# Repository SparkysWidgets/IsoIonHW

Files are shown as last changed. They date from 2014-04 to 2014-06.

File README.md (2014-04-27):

Welcome To: IsoIon Hardware Repo!!
================================

##### Note: This is for the IsoIon Hardware Version 01 Branch

IsoIon Hardware Design Files in EAGLE. IsoIon is the first and only fully open source ISE interface with galvanic isolation. It only requires a single supply on the primary end, meaning no more pesky dual supply solutions with wallwarts or DC-DC converters everywhere. IsoIon is an Ion Selective Electrode Interface with 127 steps of programmable gain control which allows it to adapt to most ISE style probes. Great care was taken during part selection to create the best all around solution with great performance for the price. All components have been proven over the last several months(if not years) via other projects (MinipH, ISOBreakout, I2CADCBreakout, etc...). IsoIon is meant to be used in a wide array of installations from commercial products, Arduino and RaspPi Projects to lab usage. If you need to interface pH, Galvanic DO, ORP, Nitrate, or most other ISE style probes this is the interface for you!!!! Its meant to interface most platforms and even contains a Seeed Grove style connector for easy integration into the Grove environment.
Please respect the licensing on these designs, we all loose if licensing inst followed and proper credit is not given!

Schematic and General Info
-------------------------
##### The initial schematic is a bit messy sorry will clean up.

- Most of this design is proven from my other works, this is the culmination of lots of research and testing (others have copied my work beware of their closed designs)
- Single supply Isolation is provided by the pair of AD micromodules ADUM6010 iso DC-DC converter and the ADUM1251 I2C isolation module for hotswapping I2C systems on a I2C bus 
- Analog front end is boosted with an I2C digital pot in place of on leg of the gain control feedback loop (this is a proper reostat digipot IC). This gives us gain control so we can select what type of probe to interface pretty ingenious Special Thanks to Practical Maker for showing me a simpler way. I just automated his method and adjusted it to match how I interface probes (We both do it slightly different, difference is good in my opinion keep up your work PM!!!!)
- Negative voltage rail generation has been slightly improved I added in an output filter network that was tested to help a bit of the noise getting through to the amplification stage.
-I've updated the design to use a fixed 3.0v precision voltage reference ad the ADC VDD/VREF input, while the op-amp will still operate at 5v rails. I am pushing us up and out of the noise floor on both rails, you won't see this much elsewhere and probably wont until this proliferates. This design still meets my requirements for 2.7 to 5.5 VIN!
- Final amp stage to ADC has been properly filtered as per TI- app notes for matching ADCs to conditioning amps
- Reverse voltage protection using Afrotechmods Pfet method! Its all about VGS vs VDS hehe!

Board Layout Info
-------------------------
##### Form factor is the same width as the Mini line but was made a bit longer to accommodate the Isolation section from my ISOBreakout designs.

- Standard 2.54mm pitch header and Grove style connector is left in place
- Careful consideration on both part placement and trace layout is very important to overall success, we are dealing with 2 fully isolated ground planes.
- DC-DC converter topologies exist on this board, some will be in close proximity to the input stage. the Negative voltage rail generator is based on a charge pump at 250Khz we want to filter this out at the -5v output, but we want only enough bypass capacitance to filter these harmonics and a bit more general op-amp operation, since we have 1uF already at the chargepump. built RC network around .1uF as close to op-amp as possible, with 1uf supply at charge pump out put. Keep these traces short and surrounded by ground plane. 
- Proper placement and layout of the analog front end is crucial to achieve best performance characteristics. Guard rings must be used around the input leg of BNC, this is so often overlooked it makes me sad. Am I the only one who reads the app-notes datasheets and op-amp books??? If your probe is going to ground to your plane(ie non differential or instrumentation topo), make sure you control the current return path (this really isnt too much of a concern on pH interfacing but other probes can source mAs)
- As per above, Op-amp is mounted underside with minimal trace length to keep complex impedances/reactances to minimum, this lets us keep all the "hot" end of amplification stage inside a guard ring. As per op-amp operation the feedback loop output(into the - pin) will drive the guard ring to the same potential as the probe input pin so everything inside the ring will have enough drive to keep it there despite noise sources and outside influences, pretty cool huh! See layout of board to get a better idea, this is how an ideal guard ring should work (including both sides as shown with the small ring on top)
- The rest of the layout is just based on functional placements with minimal trace routing work, via count inst really an issue so burn them up if you want to make really nicely couple ground planes.
- Some test pad experimentation with the obvious ones marked in new "parts" GND, V+, V- with offset and pHVout test points near their usage points.
- REMEMBER ISOLATED GROUNDS DONT CROSS THEM, take measurements from each side with respect to its ground(reference) it is important to remember or else you may burn up the isolation ICs 
- Revers voltage protection added to both header VIN inputs, using a simple p-channel mosfet to since reverse voltages and switch off.

Errata
-------------------------

##### Just a quick list of current issues
- Mostly untested as a whole, but each part has been working for a while are are mature projects
- Silkscreen  as always could use some improvements.
- Care might be needed in measuring the digipots wiper to calculate the gain more accurately
- This thing is going to be awesome and change how we think of plain old pH interfaces!!!!!

Firmware
-------------------------

- Take a look in [isoIon's Firmware Repo](https://github.com/SparkysWidgets/IsoIonBFW) For Arduino!
- Check out my USB pH interface[LeoPhi](http://www.sparkyswidgets.com/Projects/LeoPhi.aspx) for a powerful and easy to use USB PH Probe interface!

Basic Usage
-------------------------

License Info
-------------------------

<p>This is a fully open source project released under the CC BY license</p>
<br />
<span xmlns:dct="http://purl.org/dc/terms/" property="dct:title">IsoIon</span> by <a xmlns:cc="http://creativecommons.org/ns#" href="www.sparkyswidgets.com" property="cc:attributionName" rel="cc:attributionURL">Ryan Edwards, Sparky's Widgets</a> is licensed under a <a rel="license" href="http://creativecommons.org/licenses/by-sa/3.0/deed.en_US">Creative Commons Attribution-ShareAlike 3.0 Unported License</a>.<br />
Based on a work at <a xmlns:dct="http://purl.org/dc/terms/" href="/portfolio-item/ion-selective-electrode-interface" rel="dct:source">https://www.sparkyswidgets.com/portfolio-item/ion-selective-electrode-interface</a>

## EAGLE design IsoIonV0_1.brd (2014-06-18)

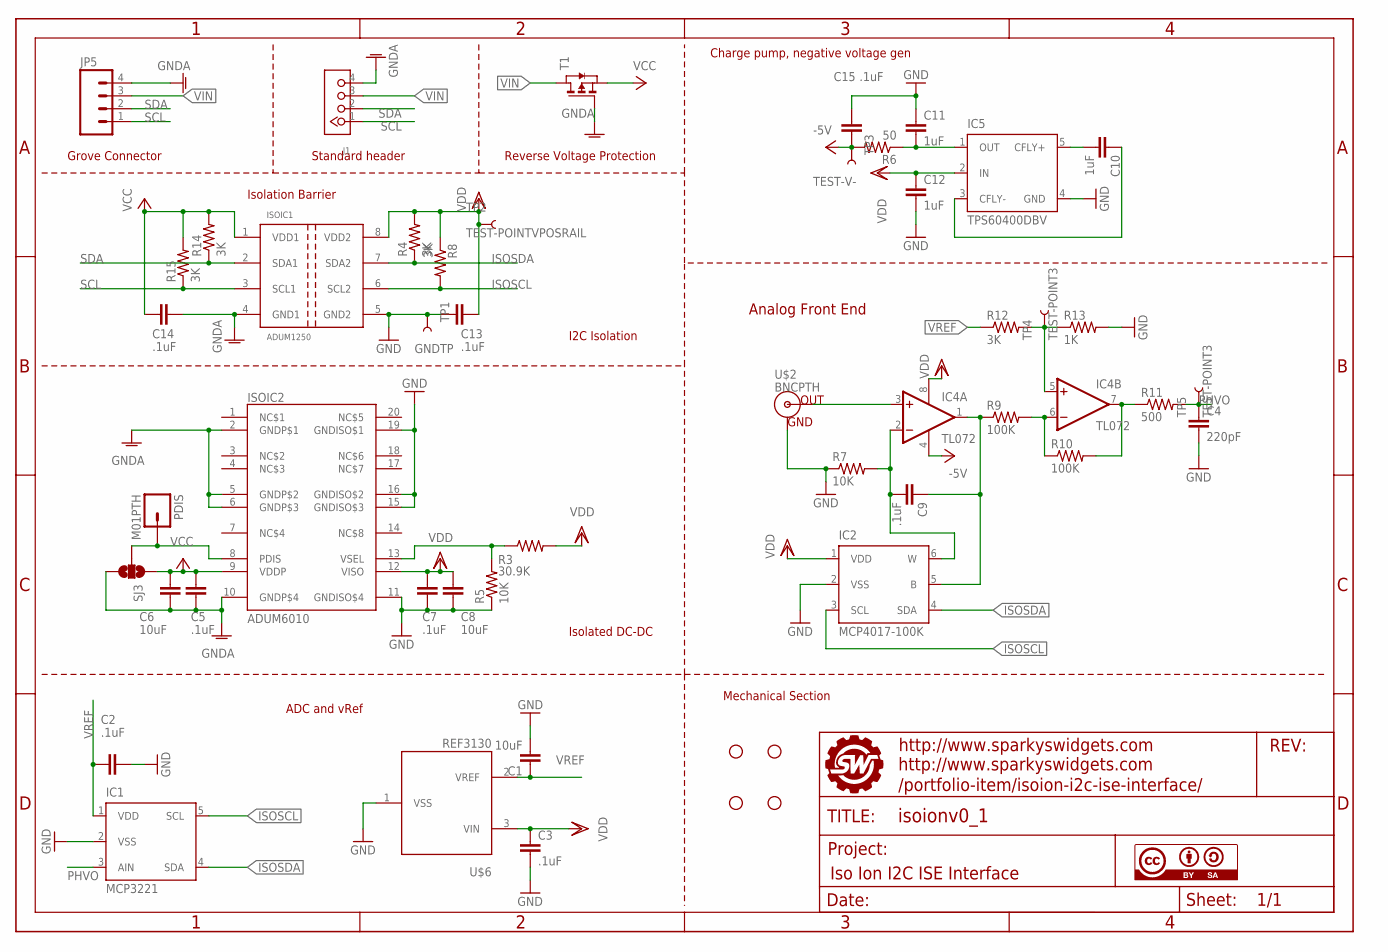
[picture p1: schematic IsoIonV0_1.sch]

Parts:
C1, C6, C8: 10uF; 0805
C2, C3, C5, C7, C9, C13, C14, C15: .1uF; 0805
C4: 220pF; 0805
C10, C11, C12: 1uF; 0805
IC1: MCP3221; SOT23-DBV
IC2: MCP4017-100K; SC70
IC4: TL072; SO08@1
IC5: TPS60400DBV; SOT23-DBV
ISOIC1: ADUM1250; SO08
ISOIC2: ADUM6010; SSOP20
J1: TWIG-4P-2.0-2.0; 4P-2.0
JP1, JP2, JP3, JP4: STAND-OFF
JP5: M04PTH; 1X04
PDIS: M01PTH; 1X01
R3: 30.9K; 0805
R4, R8, R12, R14, R15: 3K; 0805
R5, R7: 10K; 0805
R6: 50; 0805
R9, R10: 100K; 0805
R11: 500; 0805
R13: 1K; 0805
SJ3: SOLDERJUMPER_2WAYPASTE2&3; SJ_3_PASTE2&3
T1: PMOSSOT23; SOT-23
TP1: GNDTP; TEST_GND
TP2: TEST-POINTVPOSRAIL; TEST_V+
TP3: TEST-V-; TEST_V-
TP4, TP5: TEST-POINT3; PAD.03X.03
U$1: FRAME_ISOION; SWPCBLOGOWITHINFO
U$2: BNCPTH; BNC
U$3: CC-BY-SA
U$6: REF3130; SOT-23

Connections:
-5V: C15.2, IC4.4 (V-), R6.2, TP3.P$1
GND: C1.2, C2.1, C3.2, C4.2, C7.2, C8.2, C11.1, C12.2, C13.1, C15.1, IC1.2 (VSS), IC2.2 (VSS), IC5.4 (GND), ISOIC1.5 (GND2), ISOIC2.11 (GNDISO$4), ISOIC2.15 (GNDISO$3), ISOIC2.16 (GNDISO$2), ISOIC2.19 (GNDISO$1), R5.1, R7.1, R13.2, TP1.P$1, U$2.GND, U$6.1 (VSS)
GNDA: C5.2, C6.2, C14.1, ISOIC1.4 (GND1), ISOIC2.2 (GNDP$1), ISOIC2.5 (GNDP$2), ISOIC2.6 (GNDP$3), ISOIC2.10 (GNDP$4), J1.4, JP5.4, SJ3.3, T1.3 (G)
ISOSCL: IC1.5 (SCL), IC2.3 (SCL), ISOIC1.6 (SCL2), R8.2
ISOSDA: IC1.4 (SDA), IC2.4 (SDA), ISOIC1.7 (SDA2), R4.1
unnamed: IC4.5 (+IN), R12.2, R13.1, TP4.P$1
unnamed: IC4.7 (OUT), R10.2, R11.1
unnamed: IC4.6 (-IN), R9.2, R10.1
unnamed: ISOIC2.8 (PDIS), PDIS.1, SJ3.2
unnamed: ISOIC2.13 (VSEL), R3.1, R5.2
unnamed: C11.2, IC5.1 (OUT), R6.1
unnamed: IC4.3 (+IN), U$2.S (OUT)
unnamed: C9.2, IC2.6 (W), IC4.2 (-IN), R7.2
unnamed: C9.1, IC2.5 (B), IC4.1 (OUT), R9.1
unnamed: C10.1, IC5.3 (CFLY-)
unnamed: C10.2, IC5.5 (CFLY+)
PHVO: C4.1, IC1.3 (AIN), R11.2, TP5.P$1
SCL: ISOIC1.3 (SCL1), J1.1, JP5.1, R15.1
SDA: ISOIC1.2 (SDA1), J1.2, JP5.2, R14.1
VCC: C5.1, C6.1, C14.2, ISOIC1.1 (VDD1), ISOIC2.9 (VDDP), R14.2, R15.2, SJ3.1, T1.2 (S)
VDD: C3.1, C7.1, C8.1, C12.1, C13.2, IC2.1 (VDD), IC4.8 (V+), IC5.2 (IN), ISOIC1.8 (VDD2), ISOIC2.12 (VISO), R3.2, R4.2, R8.1, TP2.P$1, U$6.3 (VIN)
VIN: J1.3, JP5.3, T1.1 (D)
VREF: C1.1, C2.2, IC1.1 (VDD), R12.1, U$6.2 (VREF)

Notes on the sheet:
Grove Connector
Charge pump, negative voltage gen
Analog Front End
Isolation Barrier
Reverse Voltage Protection
Standard header
I2C Isolation
Isolated DC-DC
ADC and vRef
Mechanical Section

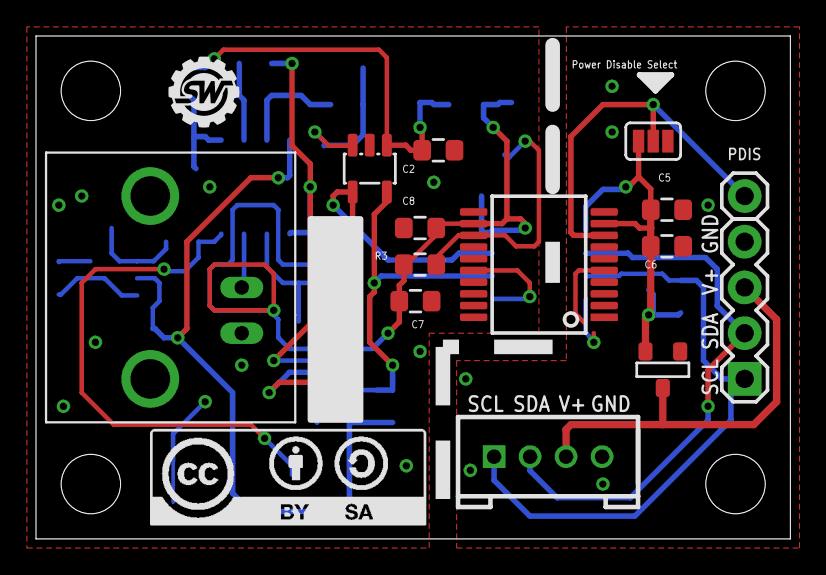
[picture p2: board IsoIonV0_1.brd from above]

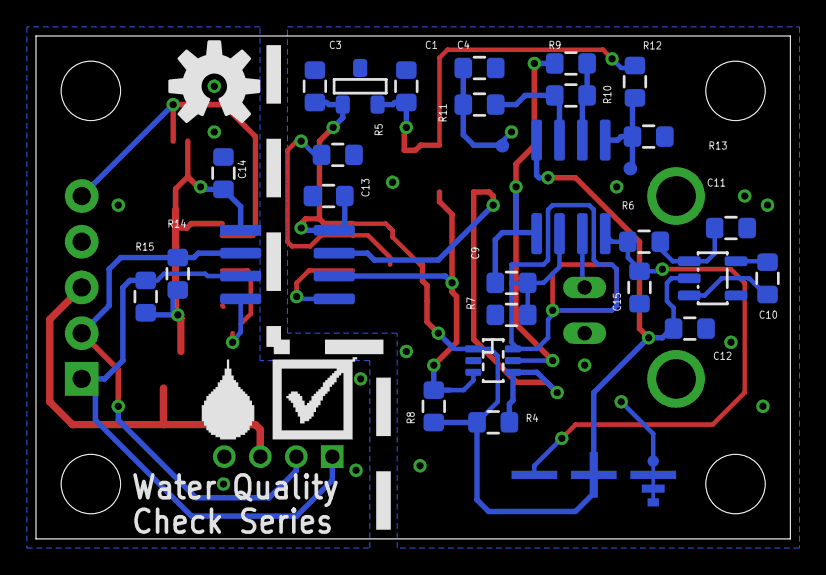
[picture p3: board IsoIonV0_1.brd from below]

Board: 2 copper layers, 41.9 x 27.9 mm, 56 parts (35 on the bottom side), 23 nets.

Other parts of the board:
U$4: OSHW-LOGO-M
U$7: SILK_ARROW
U$8: WATERCHECKLOGO2
U$9: WATERCHECKLOGO3

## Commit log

2014-04-20 Initial commit of IsoIon files, more to come oh yes much more to come!
    [IsoIonV0_1.brd, IsoIonV0_1.sch]
2014-04-21 Standoff position fixed, was incorrectly offset
    [IsoIonV0_1.brd]
2014-04-21 a minor silkscreen adjustment
    [IsoIonV0_1.brd]
2014-04-22 Cleaned up sch small silkscreen adjustment on brd
    [IsoIonV0_1.brd, IsoIonV0_1.sch]
2014-04-27 MCP4017 package updated to SC70-6
    [IsoIonV0_1.brd, IsoIonV0_1.sch]
2014-05-02 Routed Offset from VREF instead of VDD
    [IsoIonV0_1.brd, IsoIonV0_1.sch]
2014-05-02 Removed unsed VDD trace
    [IsoIonV0_1.brd]
2014-06-18 Flip pins on PMos reverse protection FET
    [IsoIonV0_1.brd, IsoIonV0_1.sch]
